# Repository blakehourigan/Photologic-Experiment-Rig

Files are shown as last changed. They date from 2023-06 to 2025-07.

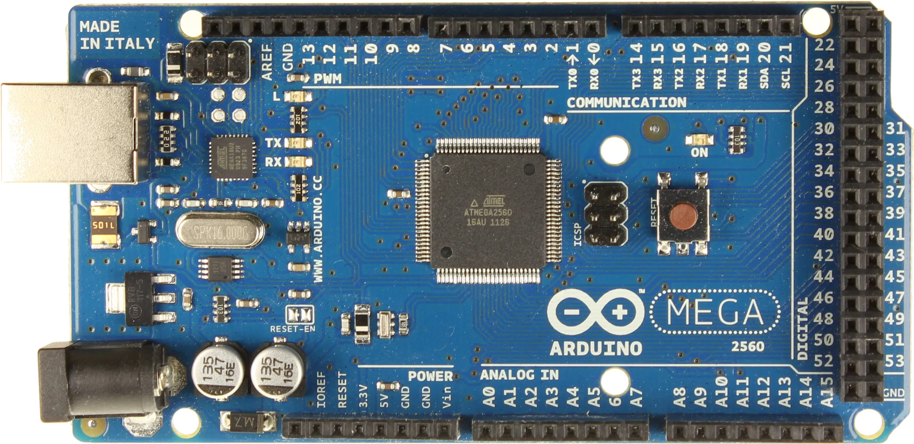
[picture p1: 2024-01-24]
Circuitry/Arduino-Mega-2560-Pinout.jpg

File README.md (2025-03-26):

# Samuelsen Lab Photologic-Experiment-Rig

## Overview
This project was created to enable novel experiments regarding smell and taste in Dr. Chad Samuelsen's research laboratory. The primary improvements that this rig provide include a photologic lick detection mechanism, and a simplified, non-motorized approach to stimulus delivery providing a more reliable experience during experimentation. 

This repository contains all files needed to reproduce a experimental rig of this type, including all 3d models, CNC machining files, code, and circuit design. 

## Features
-  **Data Accuracy** - Important event timing data such as onset, end, duration, onset relative to program start, and onset relative to trial start is measured **on Arduino Mega 2560 device** as these events occur. This ensured event timing results are accurate as viewed in the controller program.
-  **Data Representation** - Licks can be analyzed via a built in lick rasterization plot. This allows for simple visual verification of lick times relative to one another. One can ensure that licks are not occuring too close or too far apart in time. 
-  **Individual Valve / Motor Control** - Users can control each connected valve, opening or closing valves for arbitrary amounts of time. Users can also command the door motor to move up or down at any time. 
-  **Lick/Valve Prohibition** - Lick detection and valve actuation are decoupled events. A lick initiates a valve actuation, however, another lick CANNOT be detected until BOTH the valve has been closed from previous actuation AND tongue has cleared the beam (beam has restored a connection). This helps to avoid licks from occuring too close in succession. Furthermore, a continued beam break does not result in a continuous stream from a valve. A lick initiation will result in a valve opening of the determined length. This will not happen again until beam is restored and broken again. 
-  **Phantom Lick Removal** - Licks that complete in less than 10ms are disregarded and not sent to the controller (PC). This helps avoid invalid licks (due to equipment quirks) being recorded.  
-  **Simplicity** - Significant effort has been expended to ensure that software is easy to install and use. The previous model of using two Arduino boards to control the rig was found to be unnecessary. It was found to be far more effiecient to move to a one Arduino model, simplifying physical setup and communication protocols. 
-  **Speed** - Multiple threads (many cpu workers) are utilized so that GUI is always responsive regardless of logic operations underway at a given moment, without affecting the efficiency of those logic operations. 

### Required Physical Materials

- 1 Arduino Mega 2560
- 1 PC Controller Computer
- 1 Motor Logic Circuit Board
- 1 Experiment Box (3D CAD and CNC files included in this repository)
- 2 - 16 Valves and Cylinders 
 
### Assembly Instructions / Requirements for a Functioning Rig
1. **Rig Controller Code**

   **Documentation for the Rig Controller Code can be found [at this link.](https://blakehourigan.github.io/Photologic-Experiment-Rig/)**
    #### Prerequisites / Dependencies
    To use this program with the Arduino board controlling the rig peripherals (motors, optical sensors, etc) on a Windows machine, you **must** have the Arduino IDE installed. Failing to meet this dependency will result in the Arduino boards failure to connect to the controlling computer. 
    
    #### Windows Installation 
    To install the program on windows, there are two options. 
    
    1. **Exe Installer File** - To simplify this portion of the rig assembly / installation, a simple .exe installer has been provided. It can be found [here](https://github.com/blakehourigan/Photologic-Experiment-Rig/releases/tag/v1.0).
    
    2. **Running the Source Code** - For those that would rather run the program via source code, the process for getting the source code up and running can be found below.
        1. **Install Python 3.12** - This program was developed with Python version 3.12. This program is NOT guaranteed to work with any versions other than Python3.12. It can be installed [here](https://www.python.org/downloads/release/python-3120/).
        2. **Clone this repository locally on your computer** - Either by using git clone on your machine, or by clicking the 'code' dropdown on the homepage of this Github repo and downloading the .zip file, download this repository onto your machine.
        3. **Setup the Virtual Environment** - Once you have the repo locally on your machine, navigate to the controller code directory at `Photologic-Experiment-Rig\Code\Photologic Rig Main Application Code`. Once here, you can setup a virtual environment that will contain all depencies for the program by running the following command in a terminal window at this directory: `python -m venv venv'. This may take a few moments.
        4. **Activate the Environment** - Once the virtual environment is setup, you can activate it by running the following command.
            - **Windows** -> `venv\Scripts\Activate`
            - **Linux** -> `source venv/bin/activate `
        6. **Install the Dependencies** - This program is dependent on many external libraries to function properly. Under the 'Photologic Rig Main Application Code' directory, you will also find a file called requirements.txt. It contains all depencencies and their versions in a simple text file. You can install all of these dependencies at once by running the command `pip install -r requirements.txt`.
        7. **Run the Program** - You are now ready to run the controller program. Locate the file 'main.py' under the /src directory and run it by running the command `python main.py`, the program should now startup.

    #### Running the Program on Linux-based Systems
    There is no installation file for linux-based systems. Follow the 'Running the Source Code' steps described above.

    #### Building an Executable for a New Version of the Program
    For those that create new versions of the program to better suit their needs or to fix bugs that will undoubdedly arise through the usage of this program, a [Github Gist](https://gist.github.com/blakehourigan/5e176f2600446a793547babff372299c) has been put together detailing the steps you can take to create a new executable file and installer that will make installation/distribution of the program much simpler. 
    
3. **Arduino Code**
    #### Prerequisites / Dependencies
    To upload this code, you will need either the arduino-cli or the Arduino IDE. The Arduino IDE will be easiest to work with and can be found [here](https://www.arduino.cc/en/software).

    On Windows machines, the Arduino IDE is an optional package in the control software Exe installer discussed above.

    If you choose to use the Arduino IDE, you must follow these steps to ensure smooth upload of this code to the Arduino, and proper communication between the Arduino and the control software.
    #### IDE Configuration and Code Upload
    1. Once the Arduino IDE is installed, open the IDE with the Arduino Mega 2560 board connected to your PC. Your PC will recognize the board and the packages that it needs to install to communicate with it. There will be multiple pop-up windows asking if you would like to install drivers for this board. You **must** click install on all of these pop-ups. If you do not see these pop-ups and have used your Arduino board previously, you may have these packages already installed, try moving to the next step. 
    2. The code used for the Arduino in this project has one external dependency that must be fulfilled. This external dependency is the **AccelStepper** library by Mike McCauley. The version in use at the time of writing is version 1.64. You will need to install this version in the IDE. To do this, look for the library icon on the left hand side of the Arduino IDE window. It is the third button down. Once clicked, a slide-out window with the heading 'library manager' will open with a search box at the top. Click inside of the search bar and enter 'AccelStepper'. The first result should be the one you are looking for. Click the box filled with the version number (something like 1.64), and look for version 1.64. Click on this version, then click install, it should install rather quickly. Now you can now exit the library manager.
    3. Now, the Arduino code may be uploaded to the board. In the top left hand corner, click 'File', then 'Open', and search for the ArduinoCode directory in the Photologic-Experiment-Rig structure. The file you are looking for will be found at `Photologic-Experiment-Rig/Code/ArduinoCode/ArduinoCode.ino`. Locate this .ino file and double click on it to select it.
    4. Once this file is open in the IDE, ensure that your board is recognized and selected in the IDE by clicking the dropdown menu just below the 'help' section of the top bar. Here you will see any Arduino boards recognized by the PC. Select your Arduino Mega 2560 board.
    5. With the file open and your board selected, press the green upload button. It is the arrow that looks like this: '-->', the second button of three in the top left hand side of your screen. This will just take a moment, and you will see a 'Done Uploading' message in the bottom right of your screen if it completes successfully.

       **NOTE** - If you see lots of red messages and this code does not upload successfully, please make absolutely sure you installed the 'ArduinoStepper' library and that the board is connected **and** selected. You might try the board selection dropdown again to make sure of this. If this does not work, try disconnecting and reconnecting the board, and restarting your PC. 
    7. At this point your Arduino board and your PC are ready to communicate with each other for your experiments. 
 
4. **3D Printing:**

   Under contruction

5. **Machining:**   

   Under Contruction 

6. **Assembly:** 

   Under contruction

7. **Optical Fiber Setup:**   

   Under contruction

8. **Circuitry:** 

   Under contruction 

### Configuration

how to configure the system once assembled.

## Usage
A **SOP** (Standard Operating Procedure) for using this rig in an experiment can be found [here]().

## Navigating the Directory Structure
Each subdirectory in this project contains a README that explains the structure of the files contained within.

## License

This project is licensed under the MIT License - see LICENSE.txt for details.

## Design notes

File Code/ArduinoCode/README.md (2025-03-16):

# Arduino Source Code Directory

## Overview

This directory contains the code designed for the Arduino board that runs the motorized components of the 
photologic experiment rig. All licks, valve actuations, and door motor movements are orchestrated here.

## Directory Structure

An attempt was made to organize this structure such that each major component of the program is easy to find. 

### Project Root 

The project root contains the primary Arduino .ino file (comperable to main.py). This is the entry file of the program,
and can be thought of as the primary 'controller' for the Arduino code. It contains the standard 'setup' and 'loop' code 
included with most Arduino programs. 

The setup method defines input and output pins used throughout the program, while loop is the mainloop that runs continuously 
to listen for commands from the python controller program.

### Src Directory 

This directory contains headers and implementations for all primary aspects of the program. While the root file simply calls
logical functions, these directories and files provide the implementation for all this logic. 

**exp_init** - Contains logic regarding program initialization including receiving important program variables such as 
the valve schedules and opening durations for each side, as well and number of valves in use and number of trials.

**optical_detection** - This directory contains functions that detect breaks and reconnections in the optical beam, as well 
as updating the state of the lick indicator leds.

**reporting** - Here you'll find files that define the structure of the data reporting of the Arduino. It calculates event 
timing and sends it back to the controller program.

**valve_control** - Contains methods for interacting with valves. Includes methods for opening /closing single vs many valves.

**valve_testing** - Contains the logic for valve testing procedure as well as valve priming functionality.

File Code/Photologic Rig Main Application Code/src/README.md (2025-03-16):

# Source Code Directory Structure

This directory contains all source code for the program, as well as all configuration dependencies that are needed to run the program. These configuration files, along with other program 'assets' such as the program rat icon are located here. 

## MVC Architechture
An attempt was made to follow the Model-View-Controller architechture as closely as possible. In this model, 
the controller files manage interation between different components of the program. For example, models (data) 
should not interact directly with any view (GUI windows). These interations are instead managed through controller 
files. Somewhat confusingly then, the main 'controller' in this program is not in the controller directory but is 
instead called 'app_logic' and resides in the root of the /src directory. I felt this made the most sense as 
it is the source or the root of all other actions and files. As such it is placed at the root.

## Models
The models are the first classes instantiated when the program starts because all other classes require some access 
to the data that is held here. Global program variables that are passed around to various classes during 
program and experiment execution are stored here. Here you'll find data specific to different parts of the program, 
including 'experiment_process_data.py' where data regarding experiment specific data such as schedule generation, 
maximum runtime calculations, program schedule dataframe data (trial, licks per port, stimuli on a given trial, etc),
etc.

Continuing along these lines you'll find data specific to the arduino, detailed data on program events (door movements, lick times), and stimuli specific data in their respective directories.

## Views 
Finally, you'll find the views directory. As you might imagine, this directory contains all code involving the 
interactive Graphical User Interface (GUI). Every peice of code that defines something that a user interacts with 
or looks at is defined here. As before, the files have descriptive names that reveal which task they perform. 

## Controllers
This directory contains controllers other than the primary controller. Which at the time of writing contains only
the Arduino controller files. This handles interactions between Aduino specific data (models/arduino_data.py) and
Arduino specific actions. The primary action handled here is communication between the Arduino board and this 
program.

I hope that this structure proves easy to understand and navigate. I thought a lot about, and worked hard to ensure
that this would be the case.

-BH

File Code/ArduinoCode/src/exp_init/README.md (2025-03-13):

# Experiment Initialization Code

## The code in this directory is related to variables and functions that prepare the arduino for a new experiment.

### Primary functions include:

- Recieve experiment variables such as number of experiment trials and number of experiment stimuli. 
- Experiment variables allow the Arduino to safely receive the experiment valve schedule so that the required valves actuate during their assigned trial(s).
- Experiment variables also allow for safe receiving of valve opening time durations so that the Arduino knows how long to leave a valve open to get a desired 
amount of stimulant (generally 5 microliters).

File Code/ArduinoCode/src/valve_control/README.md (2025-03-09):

## VALVE CONTROL Motor Arduino Code 
This dir contains code that is designed to actuate the experiment stimuli valves. The lick_handler method is called from MotorArduinoCode.ino
and is passes a valve number (0-7), a PORT, and a duration. The code then decides which valve to actuate given valve_num, num_stimuli, and PORT.

The code will delay here for the duration passed in to the file, then will untoggle all valves and return control to MotorArduinoCode.ino.

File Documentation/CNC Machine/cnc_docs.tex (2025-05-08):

\documentclass{article}

\usepackage{hyperref}
\usepackage{listings}
\usepackage{xcolor}
\usepackage{graphicx}
\usepackage{subcaption}
\usepackage{placeins}
\usepackage{pdfpages}

\graphicspath{{"/home/blake/Pictures/arduino migration guide"}}

\setlength{\parskip}{1em}

\title{Samuelsen Lab \\ CNC Machine Operation}
\author{Blake Hourigan}
\date{April 28, 2025}

\lstset{
    basicstyle=\ttfamily\small,
    breaklines=true,
    numbers=left,
    numberstyle=\tiny,
    frame=single,
    keywordstyle=\color{blue},
    commentstyle=\color{gray},
    stringstyle=\color{orange},
}
\lstdefinelanguage{yaml}{
    morekeywords={true,false,null,y,n},      % Add keywords here
    sensitive=false,                        % Case insensitive
    morecomment=[l]{\#},                    % Line comments start with #
    morestring=[b]",                        % Double-quoted strings
    morestring=[b]',                        % Single-quoted strings
}

\begin{document}
\maketitle
\clearpage
\tableofcontents
\clearpage

\section{Obtain a Model to Machine}
Before telling the machine what path to take and what setting to use to cut out a certain part, the user must decide which part to cut, find the Solidworks part file or Fusion360 `step' file, 
generate a `drawing' (dxf) file and then layout this drawing file in the 'Carbide Create' application so that machine understands what part is being cut out, how large the stock piece is, 
and where to cut into this stock piece. 

An exception to this general rule is the case where a `C2D' toolhead path file has already been generated for a given part. If this is the case for your part, skip to Section... REFERENCE 
THE SECTION FOR CHECKING AND RUNNING AN OPERATION HERE!!!!!!!!!!!!!!!!!!!!! An example of when this will be the case includes the CNC files for all models created for the `Photologic 
Experiment Rig' and can be found in the `Rig Assembly Files' directory of the Rig's GitHub repo found \href{https://github.com/blakehourigan/Photologic-Experiment-Rig}{here}.

\section{Obtain a Drawing File for this Model}

\section{Toolhead Settings for Given Materials}

\section{Fixing the Materials to the Machine}
\section{Running a .C2D File on the CNC Machine}

\end{document}

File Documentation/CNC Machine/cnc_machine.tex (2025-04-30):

\documentclass{article}

\usepackage{hyperref}
\usepackage{listings}
\usepackage{xcolor}
\usepackage{graphicx}
\usepackage{subcaption}
\usepackage{placeins}
\usepackage{pdfpages}

\graphicspath{{"/home/blake/Pictures/arduino migration guide"}}

\setlength{\parskip}{1em}

\title{Samuelsen Lab\\CNC Machine User Guide}
\author{Blake Hourigan}
\date{April 30, 2025}

\lstset{
    basicstyle=\ttfamily\small,
    breaklines=true,
    numbers=left,
    numberstyle=\tiny,
    frame=single,
    keywordstyle=\color{blue},
    commentstyle=\color{gray},
    stringstyle=\color{orange},
}
\lstdefinelanguage{yaml}{
    morekeywords={true,false,null,y,n},      % Add keywords here
    sensitive=false,                        % Case insensitive
    morecomment=[l]{\#},                    % Line comments start with #
    morestring=[b]",                        % Double-quoted strings
    morestring=[b]',                        % Single-quoted strings
}

\begin{document}
\maketitle
\clearpage
\tableofcontents
\clearpage

\section{Sourcing a Part File (Finding the File to Cut a Shape)}
\subsection{The End Goal}
What you will eventually need to obtain to run a cutting operation on the Shapeoko Pro CNC machine is a \textit{C2D} file. You can identify these files
by their file \textit{extension}. What this means is that CNC machine files will look something like \textit{`part\_name\_here.c2d'}.

Some parts, especially those which have already been cut out before using the Shapeoko Pro CNC machine will already have a c2d file (also referred to 
in this document as a \textit{toolpath} file). If this is the case and you have located the C2D file for your part you can move on to Section 
\ref{sec:verifying-toolpath}, where the process of verifying and modifying existing toolpaths is detailed.

For newly created parts, a C2D file will not exist. You will need to obtain or create a \textit{part file} containting the dimensions of the part 
that you would like to cut out. Then, from this part file, you will need to generate a \textit{`dxf'} file. This `dxf' file will contain the 
two-dimensional representation of some `face' of a part, which will allow you to create a `toolpath' that will cut this `face' out from your stock. 

So, to briefly summarize, to cut a part out from a piece of stock on the Shapeoko Pro CNC Machine, you need a C2D file. This file may or may not already
exist. If it does exist and you have located the file, you can modify this for your particular piece of stock and cut it out. If it does not exist you
will need to create it. To create a C2D you need:
\begin{itemize}
    \item A part file (Solidworks SLDPRT or Fusion360 STEP). This can be created by you or sourced from online. But you need to be reasonable about 
        what you can cut out on our machine. The simpler the better.
    \item A \textit{dxf} file. This is a 2d representation of some side or `face' of the part that can be cut out by the CNC. 
\end{itemize}

Once you have obtained the dxf file, you can place it in a tool called \textit{Carbide Create} to define the toolpath. This is discussed further 
in Section \ref{sec:create-toolpath}.

\subsection{What is a Part File?}
A part file is a file used for 3d modelling purposes. There are many types of files such as \textit{SLDPRT} files, \textit{STEP} files, \textit{STL} files
and more. These are all similar in that they represent a 3d object in digital form. Most importantly for our use case, they contain information about 
objects including the \textit{dimensions} of the part we would like to cut out in the real world. 

\subsection{Where do Part Files Come From?}
The type of file that interests us for the purposes of creating a C2D file are SLDPRT files, which are files created for parts inside of the 
Solidworks 3d modelling program, OR STEP files, which can be used in Solidworks or Autodesk Fusion360. These parts can be created by you or someone 
else in the lab, or can be downloaded from the internet. The important part is that the file is a SLDPRT or STEP file.

\subsection{Obtaining the DXF File}
Both Solidworks and Fusion360 have... 

\subsubsection{Obtaining the DXF File from Solidworks}

\subsubsection{Obtaining the DXF File from Fusion360}

\section{Creating a Toolpath (Making a C2D File)}
\label{sec:create-toolpath}

\subsection{What is a Toolpath?}
A toolpath, as has been referred to many times in this guide, is the path the toolhead/router/machine bit will take to cut out your part. This file 
contains not only the path however, but also the \textit{feed rate}, which is the rate at which router will move around the material, 
\textit{plunge rate}, which is the rate at which the tool will move vertically into the material, 
\textit{RPM of the spindle} which is the rate at which the spindle will rotate during certain portions of the operation, etc. 

All of these attributes are important to get right to get a good finish from your operation. They also change depending on what \textit{material} you 
are cutting. Settings that have been found to work well with the two primary materials that are cut in the lab are discussed in detail in 
Secition \ref{sec:modifying-toolpath-attr}.

\subsection{What Tools will I Use?}

\subsection{Verifying Toolpaths}
\label{sec:verifying-toolpath}

\subsection{Modifying Aluminum Toolpath Attributes}
\label{sec:modifying-toolpath-attr}

As mentioned previously, it is important to get the \textit{attributes} of the toolpath such as selected tool, Spindle RPM, feed rate, etc in the 
proper ranges for your material to ensure a sucessful cut and a clean finish around cutting edges. 

Here, we will discuss the proper settings for operations involving \textit{Aluminum}.

\subsubsection{Selecting a Tool}
In this section we discuss which tool/bit/mill to use for an operation. This is a rather simple choice compared to the other attributes, and comes down
to the size of cuts you are making with your part. Generally, a .25" end mill/bit works perfectly well for machining operations. However, scenarios 
often arise where this mill will not produce successful cuts, such as when a user wants to cut a hole less than .25" in diameter. A .25" end mill simple 
will not physically fit into this hole and therefore will not work.

In other words, the .25" end mill is useful for all cuts where it physically fits in your cutting path. If this is not the case, another end mill would 
be of use. At the time of writing this guide in April of 2025, the end mill often used as a substitute is the 1/8" end mill. 

\subsubsection{Feed Rate}

\subsubsection{Plunge Rate}

\subsubsection{Spindle RPM}

\subsection{Modifying Acryllic Toolpath Attributes}

\subsubsection{Selecting a Tool}

\subsubsection{Feed Rate}

\subsubsection{Plunge Rate}

\subsubsection{Spindle RPM}

\section{Securing the Part to the Cutting Board}
This part of the process is mostly independent of the material that you will be cutting, but one must be mindful of the material througout the 
process. This will be discussed in more detail when relevent below.

\section{Securing the Part Using Tape}

\section{Securing the Part Using Glue}
This method is generally most useful when cutting aluminum, but can be very useful with acryllic as well. When possible, it is more efficient to avoid 
using the glue method because one must clean the cutting board thoroughly each time a new stock piece (piece of material that you cut a part out of) is 
placed on the cutting board. Furthermore, one must glue the piece to the cutting board and wait for the glue to \textit{cure} which takes about 30
minutes until the part is secure enough to stay put through an entire tool path cycle.

For most acryllic tool paths, the tape method described previously works fantastically well and can be much quicker and more efficient than using the 
glue method with all its overhead. If a tool path is very complex, using much or most of the area of the stock piece, it may be useful to use the glue
method. When using aluminum, the glue method can be incredibly useful to keep the entire sheet as level as possible, which is important to achieve 
clean cuts on all cut edges.

\end{document}

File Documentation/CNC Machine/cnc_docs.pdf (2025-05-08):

# Samuelsen Lab CNC Machine Operation

Blake Hourigan

April 28, 2025

1

## Contents

1 Obtain a Model to Machine | 3
2 Obtain a Drawing File for this Model | 3
3 Toolhead Settings for Given Materials | 3
4 Fixing the Materials to the Machine | 3
5 Running a .C2D File on the CNC Machine | 3

2

## 1 Obtain a Model to Machine

Before telling the machine what path to take and what setting to use to cut out a certain part, the user must decide which part to cut, find the Solidworks part file or Fusion360 ‘step’ file, generate a ‘drawing’ (dxf) file and then layout this drawing file in the ’Carbide Create’ application so that machine understands what part is being cut out, how large the stock piece is, and where to cut into this stock piece.

An exception to this general rule is the case where a ‘C2D’ toolhead path file has already been generated for a given part. If this is the case for your part, skip to Section... REFERENCE THE SECTION FOR CHECKING AND RUNNING AN OPERATION HERE!!!!!!!!!!!!!!!!!!!!! An example of when this will be the case includes the CNC files for all models created for the ‘Photologic Experiment Rig’ and can be found in the ‘Rig Assembly Files’ of the Rig’s GitHub repo found here. (https://github.com/blakehourigan/Photologic-Experiment-Rig)

## 2 Obtain a Drawing File for this Model

## 3 Toolhead Settings for Given Materials

## 4 Fixing the Materials to the Machine

## 5 Running a .C2D File on the CNC Machine

3

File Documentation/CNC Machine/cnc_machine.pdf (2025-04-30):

# Samuelsen Lab CNC Machine User Guide

Blake Hourigan

April 30, 2025

1

## Contents

1 Sourcing a Part File (Finding the File to Cut a Shape) | 4
2 Creating a Toolpath (Making a C2D File) | 5
3 Securing the Part to the Cutting Board | 6

2

4 Securing the Part Using Tape | 7
5 Securing the Part Using Glue | 7

3

## 1 Sourcing a Part File (Finding the File to Cut a Shape)

### 1.1 The End Goal

What you will eventually need to obtain to run a cutting operation on the Shapeoko Pro CNC machine is a C2D file. You can identify these files by their file extension. What this means is that CNC machine files will look something like ‘part name here.c2d’.

Some parts, especially those which have already been cut out before using the Shapeoko Pro CNC machine will already have a c2d file (also referred to in this document as a toolpath file). If this is the case and you have located the C2D file for your part you can move on to Section 2.3, where the process of verifying and modifying existing toolpaths is detailed.

For newly created parts, a C2D file will not exist. You will need to obtain or create a part file containting the dimensions of the part that you would like to cut out. Then, from this part file, you will need to generate a ‘dxf ’ file. This ‘dxf’ file will contain the two-dimensional representation of some ‘face’ of a part, which will allow you to create a ‘toolpath’ that will cut this ‘face’ out from your stock.

So, to briefly summarize, to cut a part out from a piece of stock on the Shapeoko Pro CNC Machine, you need a C2D file. This file may or may not already exist. If it does exist and you have located the file, you can modify this for your particular piece of stock and cut it out. If it does not exist you will need to create it. To create a C2D you need:

- A part file (Solidworks SLDPRT or Fusion360 STEP). This can be created by you or sourced from online. But you need to be reasonable about what you can cut out on our machine. The simpler the better.
- A dxf file. This is a 2d representation of some side or ‘face’ of the part that can be cut out by the CNC.

Once you have obtained the dxf file, you can place it in a tool called Carbide Create to define the toolpath. This is discussed further in Section 2.

### 1.2 What is a Part File?

A part file is a file used for 3d modelling purposes. There are many types of files such as SLDPRT files, STEP files, STL files and more. These are all similar in

4

that they represent a 3d object in digital form. Most importantly for our use case, they contain information about objects including the dimensions of the part we would like to cut out in the real world.

### 1.3 Where do Part Files Come From?

The type of file that interests us for the purposes of creating a C2D file are SLDPRT files, which are files created for parts inside of the Solidworks 3d modelling program, OR STEP files, which can be used in Solidworks or Autodesk Fusion360. These parts can be created by you or someone else in the lab, or can be downloaded from the internet. The important part is that the file is a SLDPRT or STEP file.

### 1.4 Obtaining the DXF File

Both Solidworks and Fusion360 have...

### 1.4.1 Obtaining the DXF File from Solidworks

### 1.4.2 Obtaining the DXF File from Fusion360

## 2 Creating a Toolpath (Making a C2D File)

### 2.1 What is a Toolpath?

A toolpath, as has been referred to many times in this guide, is the path the toolhead/router/machine bit will take to cut out your part. This file contains not only the path however, but also the feed rate, which is the rate at which router will move around the material, plunge rate, which is the rate at which the tool will move vertically into the material, RPM of the spindle which is the rate at which the spindle will rotate during certain portions of the operation, etc.

All of these attributes are important to get right to get a good finish from your operation. They also change depending on what material you are cutting. Settings that have been found to work well with the two primary materials that are cut in the lab are discussed in detail in Secition 2.4.

5

### 2.2 What Tools will I Use?

### 2.3 Verifying Toolpaths

### 2.4 Modifying Aluminum Toolpath Attributes

As mentioned previously, it is important to get the attributes of the toolpath such as selected tool, Spindle RPM, feed rate, etc in the proper ranges for your material to ensure a sucessful cut and a clean finish around cutting edges.

Here, we will discuss the proper settings for operations involving Aluminum.

### 2.4.1 Selecting a Tool

### 2.4.2 Feed Rate

### 2.4.3 Plunge Rate

### 2.4.4 Spindle RPM

### 2.5 Modifying Acryllic Toolpath Attributes

### 2.5.1 Selecting a Tool

### 2.5.2 Feed Rate

### 2.5.3 Plunge Rate

### 2.5.4 Spindle RPM

## 3 Securing the Part to the Cutting Board

This part of the process is mostly independent of the material that you will be cutting, but one must be mindful of the material througout the process. This will be discussed in more detail when relevent below.

6

## 4 Securing the Part Using Tape

## 5 Securing the Part Using Glue

This method is generally most useful when cutting aluminum, but can be very useful with acryllic as well. When possible, it is more efficient to avoid using the glue method because one must clean the cutting board thoroughly each time a new stock piece (piece of material that you cut a part out of) is placed on the cutting board. Furthermore, one must glue the piece to the cutting board and wait for the glue to cure which takes about 30 minutes until the part is secure enough to stay put through an entire tool path cycle.

For most acryllic tool paths, the tape method described previously works fantastically well and can be much quicker and more efficient than using the glue method with all its overhead. If a tool path is very complex, using much or most of the area of the stock piece, it may be useful to use the glue method. When using aluminum, the glue method can be incredibly useful to keep the entire sheet as level as possible, which is important to achieve clean cuts on all cut edges.

7

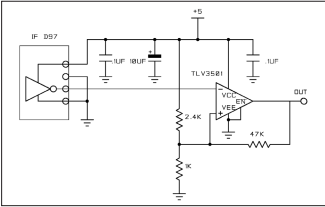
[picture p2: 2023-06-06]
Circuitry/Lick Detection Circuitry.png

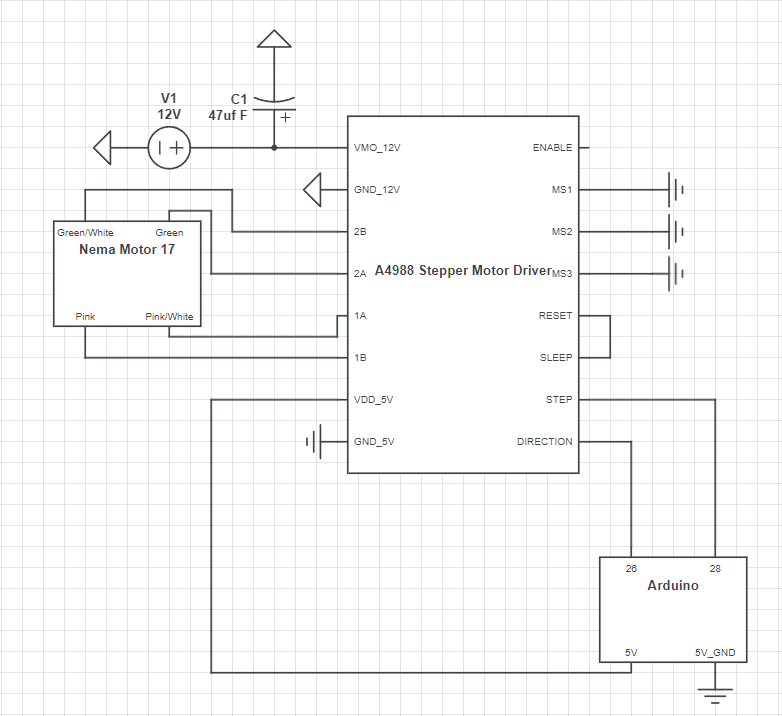
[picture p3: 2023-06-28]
Circuitry/Motor_circuit.png

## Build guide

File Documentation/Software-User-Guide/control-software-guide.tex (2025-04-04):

\documentclass{article}

\usepackage{hyperref}
\usepackage{listings}
\usepackage{xcolor}
\usepackage{graphicx}
\usepackage{subcaption}
\usepackage{placeins}
\usepackage{pdfpages}
\usepackage{xcolor}    % Required for specifying colors
\usepackage{textcomp}  % Recommended for proper straight quotes, etc.
\usepackage[T1]{fontenc}

% --- Define colors for syntax highlighting ---
\definecolor{codegreen}{rgb}{0,0.6,0}
\definecolor{codegray}{rgb}{0.5,0.5,0.5}
\definecolor{codepurple}{rgb}{0.58,0,0.82}
\definecolor{backcolour}{rgb}{0.95,0.95,0.92} % A light background color

% --- Define a custom listings style for Python ---
\lstdefinestyle{mystyle}{
    backgroundcolor=\color{backcolour},
    commentstyle=\color{codegreen},
    keywordstyle=\color{magenta},
    numberstyle=\tiny\color{codegray},
    stringstyle=\color{codepurple},
    basicstyle=\ttfamily\footnotesize, % Use typewriter font, slightly smaller
    breakatwhitespace=false,
    breaklines=true,                 % Automatically break long lines
    captionpos=b,                    % Caption position: bottom
    keepspaces=true,                 % Keep spaces, important for indentation
    numbers=left,                    % Line numbers on the left
    numbersep=5pt,                   % Distance of numbers from code
    showspaces=false,                % Don't show spaces as special characters
    showstringspaces=false,          % Don't show spaces in strings differently
    showtabs=false,                  % Don't show tabs as special characters
    tabsize=4,                       % Set tab width (Python standard is 4)
    language=Python,                 % Set the language
    morekeywords={self, dict, int},  % Add specific keywords if needed
    frame=single,                    % Add a frame around the code
    rulecolor=\color{black},         % Color of the frame
    upquote=true                     % Ensure straight quotes are used correctly
}
\graphicspath{{"/home/blake/Pictures/software-user-guide"}}

\setlength{\parskip}{1em}

\title{\textbf{Photologic Experiment Rig}\\Control Software User Guide}
\author{Blake Hourigan}
\date{March 30, 2025}

\lstset{
    basicstyle=\ttfamily\small,
    breaklines=true,
    numbers=left,
    numberstyle=\tiny,
    frame=single,
    keywordstyle=\color{blue},
    commentstyle=\color{gray},
    stringstyle=\color{orange},
}
\lstdefinelanguage{yaml}{
    morekeywords={true,false,null,y,n},      % Add keywords here
    sensitive=false,                        % Case insensitive
    morecomment=[l]{\#},                    % Line comments start with #
    morestring=[b]",                        % Double-quoted strings
    morestring=[b]',                        % Single-quoted strings
}

\begin{document}
\maketitle
\clearpage
\tableofcontents
\clearpage

\section{Introduction}
This guide provides simple overviews of included features in the Photologic-Experiment-Rig control software. It also explains the specifics of these features and how to use 
them. Some features may not have robust explanations within the software as to what \textit{type/unit} of value goes in a text box, 
what a certain value displayed in a menu means, among other various confusions. 

This guide is intended to make up for areas of the program that may lack in clarity. Each primary user interface window has its own section here that you can jump
to using the table of contents. 

\section{Installing the Software}
\label{sec:installation}
An installation guide for all software required to get the rig up and running has been written in another article. For convenience this is provided in the pages that follow.
Because the guide included is a PDF in itself, the page numbers will appear out of order until the software guide is complete.
\includepdf[pages=10-16]{"/home/blake/Documents/Photologic-Experiment-Rig/Documentation/Arduino Migration Guide/arduino_migration_guide.pdf"} 
%\FloatBarrier

\section{The Main Control Window}
\label{sec:main-control}
The `Main Control Window' refers to the user interface window that appears first upon application startup. This window is the heart of the program and is where much of the 
required experiment configuration will take place. This window is shown below in Figure \ref{fig:main-screen}. 

This window can be broken down into 5 primary sub-sections, and as such, this section of the guide is broken down into sub-sections that reflect this layout. 

\begin{figure}[h!]
        \centering
        
        \caption{The `Main Control Window' is the root of all application logic and sub-windows. It allows for navigation to these sub-windows, 
        and allows users to configure and begin experiments.}
        \label{fig:main-screen}
\end{figure}
\FloatBarrier

\newpage
\subsection{Row 1 - Start and Reset}
Row 1 contains two of the most important buttons in the application interface. Start/Stop allows a user to command the program to begin or 
terminate an experiment depending on current state. Reset allows the user to clear \textbf{all existing experiment data} and ready the application 
for a new experiment run. 

\subsubsection{Start and Stop (an Experiment)}
\label{sec:start-exp}
The start button is important because it allows the user to begin or end an experiment. Before the user can begin an experiment, 
the experiment must be fully configured. This means that all of the following steps must be completed to continue: 
\begin{enumerate}
    \item Base state  interval times (ITI, TTC, Sample, etc.), random interval times (+/- ITI, +/- TTC, +/- Sample, etc.) 
        and other configuration variables (\# Trial Blocks, \# Stimuli) \textbf{must} be defined. Discussed in Section \ref{sec:basic-configuration}.
    \item All valves must be configured with corresponding stimulus names in the `Valve / Stimuli' window. Discussed in depth in Section 
        \ref{sec:valve-stim-window}.
    \item The program schedule must be generated. Discussed in depth in Section 
        \ref{sec:valve-stim-window}.
\end{enumerate}

Once all of these requirements have been fulfilled the user can begin an experiment run. If a step has been missed, or something has 
gone wrong, the user may see a warning message such as the one in Figure \ref{fig:no-schedule}. This indicates that the program stimuli schedule has not 
yet been generated, and that the user should re-visit the 'Valve / Stimuli' window (Section \ref{sec:valve-stim-window}) 
to attempt a proper schedule generation.

If a experiment run has been started, the `Start' button will be changed to a stop button as shown in Figure \ref{fig:stop-button}. 
Pressing this button will terminate the experiment early. This will begin the standard termination process. This includes:
\begin{itemize}
    \item Halting program execution. No further experiment operations will be taken. Door will not close, program state will be 
        switched to "IDLE".
    \item Terminating the connection to the Arudino board .
    \item Preparing all accumulated data to be saved. 
    \item The user will be prompted to optionally save this data via a pop-up window in a location of their chosing.
\end{itemize}

\begin{figure}[h!]
    \centering
    \begin{subfigure}[t]{.45\textwidth}
        \centering
        
        \caption{Without an Experiment Schedule, the program isn't sure what to do. You must generate a schedule following the steps above to run an experiment.}
        \label{fig:no-schedule}
    \end{subfigure}
    \hfill
    \begin{subfigure}[t]{.45\textwidth}
        \centering
        
        \caption{Start Button is Converted to Stop Button on Experiment Start.}
        \label{fig:stop-button}
    \end{subfigure}
    \caption{}
    \label{fig:pg_admin_figs}
\end{figure}
\FloatBarrier

\subsubsection{Reset (Preparing for a New Experiment)}
The other primary button in this row of the main window is the `Reset' button. This button is important because it is \textbf{required} after 
running an experiment that the user takes either of the two following actions:
\begin{enumerate}
    \item Presses the gray 'Reset' button in the main program window. 
    \item Use the familiar red Windows `X' in the corner of the main application window to close the application session and manually 
        restart by clicking the `Photologic-Experiment-Rig' control software icon on the desktop or in the taskbar. This is the icon 
        with a cartoon rat on it. 
\end{enumerate}

Both of these actions perform the same effective operation which is to clear the data from the previous experiment and get
the program ready for a new experiment. To reiterate, pressing `Reset' will \textbf{destroy all experiment data accumulated} if the user 
has not saved this data by pressing the `Save Data' button in the fifth row of the main experiment window since the last experiment was run.
This means the user should be \textbf{very careful} when pressing this button. 

It is for this reason that when a user presses the Reset button, a warning will be displayed as shown in Figure \ref{fig:reset-confirm}. If the user selects `Yes' in this 
popup window all data will be destroyed and all windows will be closed, then the main program window will re-open automatically, ready for a new experiment.
\newline
\newline
\textbf{NOTE:} This action cannot be performed unless an experiment is \textit{not currently running}. Otherwise, you must stop the current experiment and then reset the 
application.

\begin{figure}[h!]
        \centering
        
        \caption{User must Confirm a Reset Action before it will Execute to Prevent Accidental Loss of Data.}
        \label{fig:reset-confirm}
\end{figure}
\FloatBarrier

\newpage
\subsection{Row 2 - Program Timers}
The second row of the main program window features three timers that inform the user of the following pieces of information:
\begin{enumerate}
    \item \textbf{Time Elapsed}: How long the program has been running in total
    \item \textbf{State Time}: How long the program has been in the current state (ITI, TTC, DOOR OPEN, etc.).
    \item \textbf{Maximum Total Time}: Maximum amount of time the program can possibly run.
\end{enumerate}

These timers all begin at zero until the program schedule has been generated (discussed in Section \ref{sec:valve-stim-window}) and the user 
presses the `Start' button in the main experiment window. Once an experiment has begun, this row will be populated to reflect the real values 
that belong here as shown in Figure \ref{fig:timers}.

\begin{figure}[h!]
        \centering
        
        \caption{}
        \label{fig:timers}
\end{figure}
\FloatBarrier

\newpage
\subsubsection{Time Elapsed}
This timer is the primary timer for the currently running experiment. This timer shows the time elapsed since the moment the user pressed the start button. It follows a format
of `SS | MM:SS', where the `SS' before the format separator (`|') is the \textit{total seconds} elapsed since program start time. 

Because this is a bit unwieldy and perhaps unhelpful, the information following the separator `|' shows the same figure converted to minutes 
and seconds. This allows for an easier understanding at a glance of total experiment time elapsed.

\subsubsection{State Time}
The `State Time' timer keeps track not only of the amount of state time that has elapsed since the state began, but also the maximum time it could 
possible consume. The timer follows the format of `ELAPSED TIME / TOTAL AVAILABLE TIME'. 

The only time throughout an experiment when the `TOTAL TIME' figure \textit{may} not be met is during the `TTC' time. This time can be cut short if the rat chooses to engage
in the trial. Thus the state timer may end before reaching `TOTAL TIME'.

\subsubsection{Maximum Total Time}
The `Maximum Total Time' timer is included as a convenience function that gives the user a general idea of how long an experiment could possibly take. It is almost certain to 
be inaccurate and \textit{over-estimate} the amount of time an experiment will take, because it calculates this value by \textit{summing all base interval values and random 
interval values together}. 

This means that the program assumes that all intervals --- including TTC intervals --- will use \textbf{all} of their allocated time. This is
very unlikely to be true, as the rat is likely to engage in at least \textit{some} trials. However, it still gives a general idea of the length of time an experiment 
may take.

\newpage
\subsection{Row 3 - Status Indicators}
Row 3 contains many different experiment \textit{status indicators} that inform the user of the current values of important trial variables. 
These include:

\begin{itemize}
    \item \textbf{Status (Program State)}: This indicator informs the user of the current program state ("IDLE", "ITI", "TTC", etc.)
    \item \textbf{Trials Completed (Current Trial/Total Trials)}: Displays the current trial and total trials for this experiment. Includes 
        a progress indicator to show experiment progress at a glance.
    \item \textbf{Side One: \{Stimulus\} |VS| Side Two: \{Stimulus\}}: Current Stimulus Delivery per Port (Side): Inform user which stimulus 
        is being delivered on each port (side) for the current trial. 
\end{itemize}

Examples of what these indicators look like during an experiment run are shown in Figure \ref{fig:status-indicators}. 

\begin{figure}[h!]
        \centering
        
        \caption{Status Indicators Aid the User by Informing them of the Current State of Experiment Variables.}
        \label{fig:status-indicators}
\end{figure}
\FloatBarrier

\newpage
\subsection{Row 4 - Configuring the Experiment}
\label{sec:basic-configuration}
Row 4 is one of the rows in the main window that the user will interact with the most. This row is where the user enters any desired configuration changes for an upcoming 
experiment. This row and the contained entry widgets are shown in Figure \ref{fig:entry-widgets}. 

The primary experiment variables that may change from experiment to 
experiment are the base state intervals (ITI, TTC, Sample), random state intervals (+/- ITI, +/-, TTC, etc), `\# Trial Blocks' 
(number of times each possible stimulus pairing should be delivered), and `\# Stimuli' (number of valves in use). 

\begin{figure}[h!]
        \centering
        
        \caption{The Entry Widgets in the Main Window Allow the User to Modify Default Experiment Variables.}
        \label{fig:entry-widgets}
\end{figure}
\FloatBarrier

These variables should be changed \textbf{before} the schedule is generated for the experiment. 
\newline
\newline
\textbf{NOTE}: All \textit{time-related values} (interval times) must be given in \textbf{milliseconds}. For example, 30 seconds should be 
entered in as 30000 milliseconds. 
\newline
\newline
Ensure that no entry boxes are left \textit{empty} before generating the schedule. Each box needs to 
contain some \textit{positive integer} to correctly generate the experiment schedule.

\newpage
\subsubsection{Changing Default Values}
If the default values need to be modified, this requires a change in the Python codebase. This is an involved process 
because \href{https://gist.github.com/blakehourigan/5e176f2600446a793547babff372299c}{new versions of the program need to be compiled and 
built into a new installer.}

Default values are defined in the GitHub repository directory in the file found at subdirectory
`/Code/Photologic Rig Main Application Code/src/models/experiment\_process\_data.py'
under variables named self.interval\_vars, and self.exp\_var\_entries. 

This code is shown in Listing \ref{lst:python_dicts}. Defaults can be changed here, but again a new program build and installer must be created and 
installed onto the user's machine. Users may need to ask the lab tech for assistance in this process.

\begin{lstlisting}[style=mystyle, caption={Default values can be seen Above. Time-Related Interval Values are Separated from Other Values like Number of Trials.}, label={lst:python_dicts}]
self.interval_vars: dict[str, int] = {
    "ITI_var": 30000,
    "TTC_var": 20000,
    "sample_var": 15000,
    "ITI_random_entry": 0,
    "TTC_random_entry": 5000,
    "sample_random_entry": 5000,
}
self.exp_var_entries: dict[str, int] = {
    "Num Trial Blocks": 10,
    "Num Stimuli": 4,
    "Num Trials": 0,
}
\end{lstlisting}

\newpage
\subsection{Row 5 - Accessing Other Control Windows}
Row 5 of the main program window contains 7 gray buttons that allow for navigation to other important experiment control windows. 
(Figure \ref{fig:window-buttons})

\begin{figure}[h!]
        \centering
        
        \caption{The Buttons in Row 5 Allow for Navigation to Other Experiment Windows.}
        \label{fig:window-buttons}
\end{figure}
\FloatBarrier

Descriptions of buttons and their functions will begin on the first row and column of this section. Each button in a row will be described, then the next
row will be described.

\begin{enumerate}
    \item \textbf{Valve Testing / Prime Valves}: This button allows for navigation to the `Valve Testing / Prime Valves' window. A user would
        navigate here if they desired calibrating valve opening durations via the automatic testing procedure or if they desired to 
        `Prime' the valves prior to an experimnet run. This window is discussed in depth in Section \ref{sec:valve-testing-window}.
    \item \textbf{Valve Control}: This button allows for navigation to the `Valve Control' window. A user would navigate here if they 
        desired opening or closing valves for arbitrary lengths of time. This window also allows for the manual toggling of the rig's 
        door motor to the up or down position for arbitrary lengths of time. This window is discussed in depth in 
        Section \ref{sec:valve-control}.
    \item \textbf{Program Schedule}: This button allows for navigation to the `Program Schedule' window. This is where the user would find 
        most experiment data including:
        \begin{itemize}
            \item Trial block numbers.
            \item Trial numbers.
            \item Licks-per-port for a trial.
            \item Stimulus delivered on each side for a trial.
            \item ITI, TTC, Sample times for a trial.
        \end{itemize}
            This window is discussed in depth in Section \ref{sec:program-schedule}.
    % begin row 2 
    \item \textbf{Valve / Stimuli}: This button allows for navigation to the `Valve / Stimuli' window. This is where the user navigates to 
        assign stimuli names to specific valves for the experiment. This is required to generate the experiment schedule. This window 
        and associated functions are discussed in depth in Section \ref{sec:valve-stim-window}.
    \item \textbf{Event Data}: This button allows for navigation to the `Event Data' window. This is where all data not included in the 
        `Program Schedule' window is found. A user might navigate here to view detailed data about specific events that take place during the 
        program like licks or door motor movements. This window is discussed in depth in Section \ref{sec:event-data-window}.
    \item \textbf{Rasterized Data}: This button allows for navigation to the `Rasterized Data' window. A user might navigate here to view 
        lick data per trial in a raster plot. This window is discussed in depth in Section \ref{sec:rasterized-data-window}.
    \item \textbf{Save Data}: This button is used to save all currently held data into 2 separate excel spreadsheet files. Data in the program 
        is split into 2 primary `DataFrames'. These DataFrames include the `Program Schedule DataFrame' and the `Event Dataframe'. The data 
        stored in each frame is as described previously for each respective window corresponding to these DataFrames.
\end{enumerate}

\newpage
\section{`Valve Testing / Prime Valves' Window}
\label{sec:valve-testing-window}
This window is where the user would navigate for valve opening duration calibration or valve `priming' before a experiment run. The 
`Valve Testing / Prime Valves' window is shown below in Figure \ref{fig:test-prime}.

\begin{figure}[h!]
        \centering
        
        \caption{The `Valve Testing / Prime Valves' Window opens in Testing Mode upon First Button Press.}
        \label{fig:test-prime}
\end{figure}
\FloatBarrier

\newpage

\subsection{Valve Open Duration Calibration (Running a Valve Test)}
\label{sec:valve-profiles-how-to}
This window opens in `Testing' mode by default. A user can be sure that they are in test mode if the large orange `Switch to Priming Mode' 
button is in view at the top of the window. 

In this window a user will notice several interface components that are critical to a
successful valve calibration. Calibration is important to run often to ensure that each valve is delivering the proper amount of stimulus 
on each valve in use during an experiment. The process of running a valve test procedure is described below.

\begin{enumerate}
    \item \textbf{Enter Desired Amount of Stimulus Per Lick}: First, the user should enter how much liquid that is desired each time the valve 
        opens in the entry box just below the label `Desired Dispensed Volume in Microliters (ul)'. The default value for this entry is 5
        microliters.
    \item \textbf{Enter Number of Valve Actuations}: Then, enter the number of times a valve should open and close for each test in the entry 
        box just below the label `How Many Times Should the Valve Actuate?'. 

        The default value for this entry is 1000 and is a good starting 
        point for testing. This attribute of the procedure is \textit{variable} in the event that a user wants to change this value, and 
        new duration calculations will adjust to the value input in this field. However, higher numbers will yield more accuration calculations.
    \item \textbf{Select Valves to be Tested}: Next, the user should select the valves to be tested during this procedure. This is done by 
        selecting valves via the buttons below the valve test information table. The valve test information table is the interface widget that lists all valves along
        with `Amount Dispensed Per Lick (ul)' and `Testing Opening Time (ms)' columns. Figure \ref{fig:test-buttons} shows the difference 
        between the interface with no buttons selected vs some selected.
    \item \textbf{Start Testing}: From the perspective of the interface, a test can now be started. The user should ensure that the valve 
        cylinders (vials containing stimuli for the valves) are full and all other rig specific guidelines set for the lab are now met. Once 
        the user has ensured that the physical rig is correctly setup for a valve calibration procedure, they can press the big green 
        `Start Testing' button at the bottom of the window.
        \newline
        \newline
        \textbf{NOTE}: \textit{Some} number of valves \textit{above zero} must be selected, or bugs may occur. Ensure that some valves are 
        selected before starting a test procedure.
    \item \textbf{Confirm Test Settings}: Once the user has pressed the green `Start Testing' button, they will see a new pop-up window as 
        shown in Figure \ref{fig:confirm-test}. Review the settings selected using the Valve Test Table, and the entry boxes to ensure the 
        correct settings have been selected. If all setting look okay press `Yes' to begin the procedure. Valves should be heard actuating
        on the rig. 
    \item \textbf{Enter the Amount Dispensed}: In order to understand what the opening time for the valve should be, the actual amount dispensed
        over some number of trials must be found. Find this value either by wighing the item used to collect the dispensed volume or by 
        marking the volume line on the container. Enter this value \textbf{IN MILLILITERS} in the text box pop-up that appears after a test 
        has completed. An example pop-up is shown in Figure \ref{fig:test-pop-up}. Do this for each of the valves that have been tested 
        during this cycle (1 or 2).
        \newline
        \newline
        \textbf{NOTE}: The test procedure has been designed to be flexible and adapt to each specific test. This means that each test may 
        be slightly different from the last. Specifically, the user may select any number of valves to be tested between 1-8. All valves on 
        one side can be tested and none on the other, two on each side, or any number of configurations. 

        Because of this, the user must 
        pay attention and be careful when input pop-ups appear. If there are more than zero valves remaining \textbf{on each side} to be tested,
        there will be \textbf{2 entry boxes} that appear at the end of the test cycle. \textbf{Pay attention} to which valve the program is
        asking the user to enter the dispensed volume for. This is \textit{incredibly easy} to mess up and the test will need to be restarted if 
        this happens. 

        Finally, if the user presses `Cancel' on \textbf{ANY} of the input pop-up windows, the test procedure will be cancelled and will need
        to be restarted. If the red `ABORT TESTING' button is pressed \textit{at any time} during the test procedure, the test will be 
        cancelled. Test settings can then be modified as needed and a test can be restarted. \textit{No program restart} should be necessary 
        to run multiple test procedures.
    \item \textbf{Confirm Duration Changes}: Once all valves selected for a test procedure have been tested, duration changes will be 
        \textit{automatically} calculated. Then, a new pop-up window will appear that will display the change in open duration for each
        valve that was tested. An example of this pop-up window is shown in Figure \ref{fig:results-confirm-popup}. If these changes 
        seem legitimate (no very large jumps or reductions in opening times) confirm them by pressing the green `Confirm Changes' button. 
        Otherwise, press the red `Abort Changes' button and retry the procedure.
\end{enumerate}

\begin{figure}[h!]
    \centering
    \begin{subfigure}[t]{.45\textwidth}
        \centering
        
        \caption{Default State of the Valve Test Window. Buttons not Pressed, all Valves in View in Valve Test Table.}
        \label{fig:unpressed}
    \end{subfigure}
    \hfill
    \begin{subfigure}[t]{.45\textwidth}
        \centering
        
        \caption{Valves 1, 2, 6 Selected. Valve Test Table Shows entries \textit{only} for \textit{these} Valves, Corresponding Buttons 
        Depressed.}
        \label{fig:depressed}
    \end{subfigure}
    \caption{The User will Know a Valve has been Selected when its Corresponding Button has been Depressed (pushed in), and the Valve
    Test Table has been Updated with a row that Includes the Selected Valve.}
    \label{fig:test-buttons}
\end{figure}

\begin{figure}[h!]
        \centering
        
        \caption{The User Must Confirm Test Settings before the Procedure will Begin.}
        \label{fig:confirm-test}
\end{figure}

\begin{figure}[h!]
        \centering
        
        \caption{1 or 2 Input Pop-Up Windows will Appear Depending on Number of Valves Remaing to Test on Each Side.}
        \label{fig:test-pop-up}
\end{figure}

\begin{figure}[h!]
        \centering
        
        \caption{Users can Confirm or Abort Updating the Valve Durations in the `CONFIRM VALVE DURATION CHANGES' Pop-Up Window following a
        Successful Test Procedure.}
        \label{fig:results-confirm-popup}
\end{figure}

\FloatBarrier

\subsection{Manual Valve Duration Adjustment / Duration Profiles}
Manual adjustment of valve timings or changing the selected valve timing `profile' is available by selecting the `Manual Valve Duration 
Override' button just above and to the right of the valve test information table in the `Valve Testing' window. 

\subsubsection{Why was this Necessary?}
Sometimes mistakes are made in the testing procedure. One might overlook an abnormally large adjustment in the automatic calculations that 
could cause issues with proper valve actuation during experiment runtime. Perhaps it is found that a previous duration profile seemed to
work better than the current one for one reason or another. 

Whatever the reason, it is nice to be able to restore things to working order with the press of a single button. This is the purpose of 
valve duration profiles and the manual time adjustment window. This window is pictured below in Figure \ref{fig:manual-window}. 

\begin{figure}[h!]
        \centering
        
        \caption{Users can Override Mistankenly Accepted Automatic Valve Duration Adjustments by Manually Entering New Times in the 
        `Manual Valve Timing Adjustment' window.}
        \label{fig:manual-window}
\end{figure}

\

\subsubsection{Okay, How do I do it? (Setting Valve Duration Profiles)}
Here, users can manually enter different opening times for any of the rig's currently configured 8 valves and save them as the new selected
timings by pressing `Write Timing Changes'. However, most people likely do not have the exact timing for a given valve memorized. To 
aid the user here are different valve timing profiles. To find previously configured or default profiles, click the dropdown menu in the 
top right of this window as shown in Figure \ref{fig:timing-dropdown}.

In this dropdown menu, users have the ability to set durations to one of the following profiles:
\begin{itemize}
    \item \textbf{Default}: Reset all durations back to the default value of 24125 milliseconds by writing the default profile as the new active
        profile. This is a good starting point for calibration on fresh valves.  
    \item \textbf{Last Used}: These timings are the most recently used timings and serve as the active timings for the program. At all times, 
        this profile is the one used during experiments. When new timings are written, they are written into \textit{this} profile.
    \item \textbf{Archive 1}: Archives are used as `back-ups' of older profiles. Anytime a new profile is written (automatic from a valve-test
        or manually) the previous `profile' is set to the newest slot in the archive. The newly created profile is then set as the `Last Used' 
        or current profile. 

        Each time a new archive is added, each archive moves down a slot. For example, if a user writes a new timing 
        profile, the oldest archive profile (`Archive 3') is destroyed. Then the contents of archive 2 move to archive 3 
        (`Archive 2' -> `Archive 3'). Archive 1 then follows the pattern, moving to slot 2 (`Archive 1' -> `Archive 2'). This clears the way
        for the last used profile to be moved to the most recent arhive slot (`Last Used' -> `Archive 1'). Finally, the newly created profile 
        can be set as the active profile (`Last used'). 
    \item \textbf{Archive 2}: Archive 2 is the next archival slot, the second oldest of the archive slots.
    \item \textbf{Archive 3}: Archive 3 is the final archive slot, the oldest of all archives, and is the next profile that will be destroyed 
        upon a new write.
\end{itemize}

\begin{figure}[h!]
    \centering
    
    \caption{Users can Restore old Timings via the Timing Profile Dropdown Selection Menu in the `Manual Valve Timing Adjustment' window.}
    \label{fig:timing-dropdown}
\end{figure}
\FloatBarrier

\clearpage
\subsection{Valve Priming}
\subsubsection{Why is this Useful?}
The final primary feature of the `Valve Testing / Prime Valves' Window is valve `priming'. This is a fancy way of saying "open and close the
valves a bunch of times". The reason this is an included feature is that it was found that simply leaving valves open for an extended period
of time while downstream tubes were full of \textit{only air} (in an attempt to fill them with stimulus) did \textit{not} seem to allow for 
flow to the tip as desired. 

However, it was found that rapidly opening and closing the valves repeatedly \textit{did} effectively allow for flow all the way down to the 
tip of the tubes (albeit slowly).

\subsubsection{Okay, How do I do it? (Priming Valves)}
This process is very similar to the process described in Section \ref{sec:valve-profiles-how-to}. Follow the steps below. This guide assumes
that you have the `Valve Testing' window already open on your display as shown in Figure \ref{fig:test-prime}

\begin{enumerate}
    \item \textbf{Switch to Priming Mode}: First, the user should click the orange button labelled `Switch to Priming Mode' as shown in 
        Figure \ref{fig:test-prime}. This will change the interface to look like Figure \ref{fig:priming-mode}.
            \item \textbf{Enter Valve Acutation Number}: Next, the user should enter how many times the valve should actuate (open and close) before 
        stopping. The use should enter this value in the entry box under the label titled `How Many Times Should the Valve Actuate?'. 
    \item \textbf{Select Valves to Prime}: Finally, the user should select the buttons corresponding to the valves to be primed. 
        To understand what a valve button looks like when it is selected, refer to Figure \ref{fig:test-buttons}.
    \item \textbf{Begin Prime Procedure}: The application is now ready to begin the procedure. Press the orange `Begin Priming' button to 
        begin. 
    \item \textbf{Confirm Prime Settings}: The application will generate a pop-up window similar to that shown in Figure \ref{fig:confirm-test}.
        The user should review the settings in the pop-up window to confirm these are correct. If they are correct, pressing `Yes' will 
        begin the test procedure.
\end{enumerate}
\textbf{Note}: The procedure can be stopped at any time by pressing the yellow `STOP PRIMING' button. The software \textit{does not} need to 
be reset to start a new priming procedure. Once can start and stop as many times as is necessary, changing settings if desired.

After the procedure is complete, check the tubes for the valves just primed. If stimulus has filled the tube to the tip (end nearest spout), 
then the procedure was successful and the tubes are ready for an experiment. If not, repeat the process.

\begin{figure}[h!]
    \centering
    
    \caption{Users can `Prime' Valve by Clicking `Switch to Priming Mode' in the `Valve Test' Window.}
    \label{fig:priming-mode}
\end{figure}
\FloatBarrier

\clearpage
\section{The `Valve Control' Window}
\label{sec:valve-control}
\subsection{What does this Window do?}
The `Valve Control' Window is where users can navigate to manually switch on or off valves for arbitrary lengths of time. They may also manually move the rig door up or
down in this window. The `Valve Control' window is shown in Figure \ref{fig:valve-control-example}.

\subsection{Controlling the Valves}
All valves begin in the off state and can be switched on by pressing the button corresponding to the valve the user would like to open.  
Valves will remain open until user selects this button again. 

This functionality is particularly useful 
for pressurizing valves and quickly running cleaning solution through the stimulus delivery tubes. 
\newline
\newline
\textbf{NOTE}: Be aware and mindful that the valves get \textit{very hot} when left open for long periods of time. 

\subsection{Controlling the Door Motor}
The door motor can be moved down by pressing the green `Move Motor Down' button in this window. The door can be left open or closed as long as the user would like and 
can be moved up and down as many times as necessary. 
\newline
\newline
\textbf{NOTE}: The user should \textit{wait} until the motor movement is \textit{completely finished} before pressing the button again to initiate another movement. 
\newline
\newline
Pressing 
the button before the movement has completed will interfere with the Arduino board's ability to keep track of the current location of the door and will result in the door 
moving too far out of range, potentially \textbf{damaging rig components}. Ensure movements have completed before beginning another.
\newline
\newline
\textbf{IMPORTANT}: The door motor \textbf{must be} in the \textbf{UP} position before starting an experiment. The application assumes this to be the case. If the door is 
left down, similar symptoms as described in the above note will occur. Ensure the motor is in the UP position before leaving this window and beginning an experiment run.

\begin{figure}[h!]
    \centering
    
    \caption{Users can Manually Control Valves as well as the Door Motor in the `Valve Control' Window.}
    \label{fig:valve-control-example}
\end{figure}
\FloatBarrier

\begin{figure}[h!]
    \centering
    
    \caption{Valve Buttons Turn Green on User Press Indicating Valve is Now Open. Motor Button Turns Blue upon User Press to Indicate Door is now Down.}
    \label{fig:valve-control-2}
\end{figure}
\FloatBarrier

\clearpage
\section{The `Program Schedule' Window}
\label{sec:program-schedule}

\subsection{What does this Window do?}
The `Program Schedule' Window allows the user to view one of the primary `dataframe' components where the software stores experiment data. An example of this window 
when populated with data from an upcoming experiment is shown in Figure \ref{fig:prog-sched-ex}.

\begin{figure}[h!]
    \centering
    
    \caption{The Program Schedule Window allows Users to View Basic Current Experiment Data. This Figure Shows the Window Prior to Experiment Beginning, thus the NAN Values
    for Lick Data.}
    \label{fig:prog-sched-ex}
\end{figure}
\FloatBarrier

\clearpage
\subsection{This Window won't Open due to Error... Why? (Experiment Schedule Error)}
The user may see an error when attempting to open this window if they have not yet generated the experiment schedule for the experiment run. The error one may see is shown in
Figure \ref{fig:prog-sched-err}. The steps to generate the schedule are outlined with references to specific sections in Section \ref{sec:start-exp}.

\begin{figure}[h!]
    \centering
    
    \caption{The Program Schedule window will not Open Until the Program Schedule has been Generated for the Experiment.}
    \label{fig:prog-sched-err}
\end{figure}
\FloatBarrier

\subsection{What do All these Fields Mean?}
This section explains each column, its purpose, and the data/units held within the column's rows where applicable. Columns are explained from left to right as they 
appear in the Program Schedule window.
\begin{enumerate}
    \item \textbf{Trial Block}: A trial \textit{block} is a group of trials that contain all possible pairings (unique stimuli pairings) of stimuli delivery during an 
        experiment. 
        
        For example, for an experiment with two stimuli in use for each port, (sucrose, saccarhin Port 1 | sucrose, saccarhin Port 2), each stimulus must be 
        delivered on each port. So there are number of valves / 2 pairings for a trial block. Here there would be 2 trials per block. For the first trial there may be
        Port 1: Sucrose | Port 2: Saccarhin. There must also then be the opposite of this delivery for trial two: Port 1: Saccarhin | Port 2: Sucrose. This example is shown 
        more clearly in Figure \ref{fig:prog-sched-ex}.
    \item \textbf{Trial Number}: Trial number is simply the trial number of the current trial beginning at 1 and ending at total number of trials.
    \item \textbf{Port 1}: Port 1 displays the stimulus to be delivered on Port 1 for the trial in the row.
    \item \textbf{Port 2}: Port 2 displays the stimulus to be delivered on Port 2 for the trial in the row.
    \item \textbf{Port 1 Licks}: Port 1 \textit{Licks} is updated after a trial occurs and shows the number of times Port 1 was licked for this trial.
    \item \textbf{Port 2 Licks}: Port 2 \textit{Licks} is updated after a trial occurs and shows the number of times Port 2 was licked for this trial.
    \item \textbf{ITI}: ITI shows the allocated time for ITI state for a given trial. This time is given in milliseconds. 
    \item \textbf{TTC}: TTC shows the allocated time for a TTC state for a given trial. This time is given in milliseconds. 
    \item \textbf{SAMPLE}: SAMPLE shows the allocated time for a Sample state for a given trial. This time is given in milliseconds. 
    \item \textbf{TTC Actual}: TTC Actual shows the \textit{actual time used} for a TTC state for a given trial. This is necessary because three rat licks will transition the 
        program into a Sample state early, and will not use all allocated TTC time. This time is given in milliseconds. 
\end{enumerate}

\clearpage
\section{The `Valve / Stimuli' Window}
\label{sec:valve-stim-window}
\subsection{What Does this Window Do?}
The `Valve / Stimuli' Window is where users should navigate to label the stimuli that will be delivered for a given valve. This is an important step to generating the program 
schedule as described in Section \ref{sec:start-exp}. The `Valve / Stimuli' window as it will be found on first open is shown in Figure \ref{fig:valve-stim}.

\begin{figure}[h!]
    \centering
    
    \caption{The `Valve / Stimuli' Window is Initially Filled with Default Values Corresponding to the Labelled Valve Number of a Valve.}
    \label{fig:valve-stim}
\end{figure}
\FloatBarrier

\subsection{How Do I Use this Window? (Generating an Experiment Schedule)}
The `Valve / Stimuli' window is where the stimuli schedule is generated for an upcoming experiment. This process will generate not only stimulus lineup for each port 
per trial for the experiment, but also state base interval times (ITI, TTC, etc) and 
the random times to be added to these base times. Assuming that interval times and other experiment configuration variables have been set as desired in the main 
program window (Section \ref{sec:basic-configuration}), the remaining step prior to schedule generation is naming the stimuli for each valve. 

When assigning stimuli names to valves, the user should start at valve one and continue downwards (enter only in new rows, do not enter in column two). This will simplify
the process, as the program will automatically assign names to valves on column two based on names entered in column one. When names have been assigned, users can press the
large green `Generate Schedule' button at the top of the `Valve / Stimuli' window.

If this process is successful, the `Valve / Stimuli' window will disappear, and a new `Program Schedule' window will appear displaying the schedule to be followed for the 
next experiment as shown in Figure \ref{fig:prog-sched-ex}.

\clearpage
\section{The `Event Data' Window}
\label{sec:event-data-window}
The `Event Data' Window shows the user more detailed information about events that occur during an experiment run. While the program schedule shows much of the desired 
information about the experiment to the user, it lacks information like event timestamps, durations, etc. The `Event Data' window fills in these data gaps. 

Details about rat licks as well as door motor movement details are contained in this window. Because two different event types are stored here, some columns may not always 
contain a value. This is discussed in more detail below.

\begin{figure}[h!]
    \centering
    
    \caption{The event data window }
    \label{fig:event-window-ex}
\end{figure}
\FloatBarrier

\subsection{Detailed Column Breakdown}
Here the contents of each column is discussed in detail. This includes general details as well as units of displayed information where applicable.

\begin{enumerate}
    \item \textbf{Trial Number}: This column displays the trial that an event occurred in. 
    \item \textbf{Licked Port}: This column will \textbf{not} always contain a value. It will only be filled if the event being recorded is a rat lick. Motor movement 
        recordings will mark this columns value for this row as `nan'.
    \item \textbf{Event Duration}: This column is used for \textit{both} licks and motor movements. It records the length of time the event occurred in from onset to offset. 
        
        For licks, this is the time difference between the moment the lick beam is broken until the moment it is restored. For door motor movements, it is the time 
        difference between motor movement instruction until the motor reaches the target position. This time is represented in \textbf{milliseconds}.
    \item \textbf{Valve Duration}: Valve duration is only marked for the subset of lick events that occur within the `SAMPLE' state. This is because valves are not 
        opened during `TTC' state. Value stored as nan for licks in `TTC' state or motor movement events. This time is represented in \textbf{milliseconds}.
    \item \textbf{Time Stamp}: This value is the time the event occurred relative to the program start time (t=0) in \textbf{seconds}.
    \item \textbf{Trial Relative Stamp}: This value is the time the event occurred relative to the trial start time. Trial start here is defined as TTC start time, because 
        this is the moment the rat can begin to engage in the trial. This time is represented in \textbf{seconds}.
    \item \textbf{State}: State can hold different values depending on the \textit{type} of event that occurred. Motor movements will state the \textit{type} of motor movement 
        that occurred (MOTOR [UP, DOWN]). Licks will show the program state at the time of the lick (TTC, SAMPLE).
\end{enumerate}
\textbf{NOTE}: The method by which data in this window is refreshed is pressing the `Event Data' button in the main program window. This button serves as the method to 
access the window and update with new information that has occurred. The window will \textbf{NOT} automatically refresh. The user must manually trigger updates via this 
method.

\clearpage
\section{The `Rasterized Data' Window}
\label{sec:rasterized-data-window}
Pressing the `Rasterized Data' button in  the main program window produces two identical raster plots representing the licks per trial per port. This window is useful to 
ensure that reported licks from the Arduino board seem to match with the accepted understanding of how quickly rats can lick maximally. 

In other words, it allows users to
ensure that the data being recorded is accurate, and no `phantom licks' are being recorded due to equipment inadequacies or failures.

In this window, the Y-axis represents trial number, while X-axis values represent the time stamp associated with a given lick.

\begin{figure}[h!]
    \centering
    \begin{subfigure}[t]{.45\textwidth}
        \centering
        
        \caption{Example of Data Filling the Side (Port) 1 Raster Plot.}
        \label{fig:raster-1}
    \end{subfigure}
    \hfill
    \begin{subfigure}[t]{.45\textwidth}
        \centering
        
        \caption{Example of Data Filling the Side (Port) 2 Raster Plot.}
        \label{fig:raster-2}
    \end{subfigure}
    \caption{Raster Plots are Seperated by Port to make Analysis more Straightforward.}
    \label{fig:rasters}
\end{figure}

\end{document}

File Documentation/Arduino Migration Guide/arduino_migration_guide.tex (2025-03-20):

\documentclass{article}

\usepackage{hyperref}
\usepackage{listings}
\usepackage{xcolor}
\usepackage{graphicx}
\usepackage{subcaption}
\usepackage{placeins}
\usepackage{pdfpages}

\graphicspath{{"/home/blake/Pictures/arduino migration guide"}}

\setlength{\parskip}{1em}

\title{\textbf{Photologic Experiment Rig}\\Arduino Migration Guide}
\author{Blake Hourigan}
\date{March 18, 2025}

\lstset{
    basicstyle=\ttfamily\small,
    breaklines=true,
    numbers=left,
    numberstyle=\tiny,
    frame=single,
    keywordstyle=\color{blue},
    commentstyle=\color{gray},
    stringstyle=\color{orange},
}
\lstdefinelanguage{yaml}{
    morekeywords={true,false,null,y,n},      % Add keywords here
    sensitive=false,                        % Case insensitive
    morecomment=[l]{\#},                    % Line comments start with #
    morestring=[b]",                        % Double-quoted strings
    morestring=[b]',                        % Single-quoted strings
}

\begin{document}
\maketitle
\clearpage
\tableofcontents
\clearpage

\section{Why the Migration?}
If you are not interested in why but only \textit{how to perform} the migration, skip to Section \ref{sec:migration}.

When I began working on this project again after about a year-long hiatus, I was struck by various aspects of the program that were much less effiecient than they should be. 
I began work to resolve some of these issues individually on
the two different Arduino boards. I changed data structures, algorithms, moved to simpler structs rather than classes, etc. and I noticed incredible speed-ups in the tasks being 
performed on each board. As things became faster and more efficient, I began to wonder if having \textit{two distinct Arduino boards} was necessary. 

The processor on board is incredibly fast and the tasks being performed are so light that it seemed like overkill to
have two individual boards performing different tasks. Not to mention the overhead of having two separate boards. Handling communication between two different boards meant that code
was required to identify these boards. Often commands needed to be sent to two boards at once rather than combining commands to one board. Furthermore, the Arduino boards needed 
a mechanism to communicate with \textit{each other}. The Laser Arduino needed to somehow communicate the fact that a lick has occurred so that the Motor/Valve Arduino could 
properly respond.

So I became interested in the idea of simplifying this setup. It was just a test at first, but it quickly became clear that this setup would perform similar to, if not better than the 
previous setup. With the added benefit of being able to easily collect and send lick, valve, \textbf{and} motor timestamp data in one place. This allowed for much easier communication 
of this data to the controller program. 

The most difficult part of the process was creating a algorithm for detecting licks, opening valves, and marking closing times while prohibiting 
lick detection until this marking occured. The real complication here was that the algorithm could not \textit{loop or \textbf{block}} the execution of the rest of the code. 
But once this was finished and various pieces of code were optimized
for speed (e.g properly ordering command conditional statements) and testing simulated licks with an onset-to-end duration of as low as 15ms, it was clear that the board could handle these
tasks all together. It is able to record and report these data points, handle door motor operation, valve operation, and lick detection all in the same board. 

This allows for a simpler setup and slightly lower cost of the rig. But the real benefit here is a greater wealth of data and reduced complexity in communication protocols and physical setup. 

For the rest of this article I will detail the steps you must take to migrate your setup from 2 Arduino boards to 1, including hardware and software steps.

\section{The Migration Process}
\label{sec:migration}
I've worked quite hard during this period of development to make distribution of both of the required software packages for the rig as simple and easy as possible. While the Arduino portion of the code is 
slightly more complex, I've tried to detail every step as simply and as verbose as possbile to ensure that anyone can do it. If you follow each step closely, you should be up and running
in no time!

If you are someone who is savvy enough, you may use the KiCAD PCB design file, along with the new Arduino source code files to assist you during this process. These are \textbf{NOT} 
required to complete the migration, but they may be helpful if you get confused or make a misstep along the way. 

If you have downloaded the \href{https://github.com/blakehourigan/Photologic-Experiment-Rig}{Github repository} locally on your computer, the KiCAD project 
file you are looking for will be located at `/Circuitry/Final\_PCB.kicad\_pro'. The Arduino Code is Located at `/Code/Arduino Code'. The root Arduino `.ino' file will be located here, 
with specific function code such as optical sensor pin definition and LED pin definition located under the respective directory inside of the /src directory.

\subsection{Hardware Migration Steps}
First, we will start with the hardware migration steps. Here you are going to eventually remove the Arduino board previously labelled 'Laser Arduino', leaving only the Arduino board previously 
labelled or known as the `Motor Arduino'. If you don't know which is which, identification steps are given below. 

\subsubsection{Identify the `Laser Arduino' Board}
You are going to first identify which Arduino board is the `Laser Arduino' in your setup. If the board is unhelpfully \textbf{not} labelled, it is the board with wires running 
to the PCB (circuit board) whose connectors are labelled 
`Laser\_Power\_Pins1' and `LED\_Logic\_Harness1'. One-by-one, we will migrate every connection here to the board previously known as the `Motor Arduino'.

You \textbf{do not need to remove} the actual connectors on the PCB, that will only complicate the process unnecessarily. 

\subsubsection{Obtain a Small flat-head Screwdriver}
Locate the small flat-head screws that sit atop the Arduino screw terminal boards shown in Figure \ref{fig:ino-terms} that secure the non-connector (loose wire) end to the 
Arduinos. Again, we will remove these wires \textbf{ONE AT A TIME} to simplify this process.

\begin{figure}[h!]
        \centering
        
        \caption{The Arduino Terminal Screws Sit atop the Arduino Board, and Face Away from You if You Look at the Arduino Head On.}
        \label{fig:ino-terms}
\end{figure}
\FloatBarrier

\subsubsection{Remove Unnecessary Connectors}
Now we are going to remove the wires that connect to both Arduino boards that facilitate communication between them. 
\begin{enumerate}
    \item \textbf{Digital Pin 8} - We will begin with digital pin number 8 which functioned as the lick side indicator previously. This pin should be the same on both Arduino boards.
        \begin{enumerate}
            \item \textbf{Locate Digital Pin 8} - Locate the wire attached to digital pin 8 on the \textbf{`Laser Arduino' board}. It is the terminal with the big number 8 on it and the 
                square will be black.
            \item \textbf{Unscrew the Terminal} - Unscrew the terminal with your screwdriver and remove the wire. Follow the wire to the connection on the `Motor Arduino' and repeat 
                the process.
            \item \textbf{Tighten the Terminal Screw} - Tighten the terminal screw back down on both Arduino screw terminal boards. 
        \end{enumerate}
    \item  \textbf{Digital Pin 7} - Next, we will remove digital pin 7 which functioned previously as the lick detected signal. This pin is slightly different because it is 
        \textbf{not the same} on both boards. It is pin 7 on the `Laser Arduino', and is pin number 2 on the `Motor Arduino'.
        \begin{enumerate}
            \item \textbf{Locate Digital Pin 7} - Locate the wire attached to digital pin 7 on the \textbf{`Laser Arduino' board}. It is the terminal with the big number 7 on it and 
                is shaded black.
            \item \textbf{Unscrew the Terminal} - Unscrew the terminal with your screwdriver and remove the wire. Follow the wire to the connection on the `Motor Arduino' and repeat 
                the process.
            \item \textbf{Tighten the Terminal Screw} - Tighten the terminal screw back down on both Arduino screw terminal boards. 
        \end{enumerate}
\end{enumerate}
\subsubsection{Migrating the Remaining PCB Connectors}
Now that we have removed the inter-Arduino communication connections, we just need to migrate the `Laser Arduino' PCB connector wires to the `Motor Arduino'. 
As dicussed above, these include the below connections from the PCB. As before, we will move wires one-by-one starting at the top of the list and moving downwards.
\begin{enumerate}
    \item \textbf{Laser\_Power\_Pins1}\\
        This connector is the easier of the two to migrate. It is just two connectors, 5V and GND. 
        \begin{enumerate}
            \item \textbf{Locate the 5V Wire} - This wire should have red tape wrapped around it and run to a 5V terminal on the `Laser Arduino' board.
            \item \textbf{Remove the Wire from Screw Terminal} - Unscrew the terminal screw that this wire runs to on the `Laser Arduino', and remove the wire from the terminal.
            \item \textbf{Locate a Free (unused) 5V Terminal on `Motor Arduino'} - Find a free 5V slot on the `Motor Arduino' and unscrew the terminal screw. 
            \item \textbf{Secure the Wire into the Terminal} - This step is likely to be one of the more challenging parts of the migration.
                The wire may not reach because it was not originally designed to stretch that far. You may have to play with the location of the `Motor Arduino' board 
                or solder extra wire to get it to reach. 

                \par Once you have situated the boards such that all wires reach their terminals, insert the wire into the 
                open terminal and fasten the wire by tightening the screw until the wire is secure and will not pull from its terminal. 

                \par \textbf{NOTE}: You should pinch the wire with your finger and twist the end around until all 
                of the wire is bundled together cleanly to avoid the wire touching another terminal or not fitting into the terminal well. You should do this every time you 
                insert a wire from this point forward.

            \item \textbf{Locate and Unscrew the Terminal for the GND Wire} - Now, take the other wire from the same connector (the one not wrapped in red tape) and remove it from its screw terminal on the `Laser Arduino'.
            \item \textbf{Locate a Free GND Terminal on the `Motor Arduino'} - Locate a open GND Terminal on the `Motor Arduino', unscrew the terminal, insert the wire, and tighten the screw until 
                the wire is secure and will not pull from its terminal.
        \end{enumerate}

    \item \textbf{LED\_Logic\_Harness1}\\
        Now we are almost done with the hardware migration process! We have just the 4 wires on the LED\_Logic\_Harness1 connector left to go. These wires are easier to 
        differentiate as they are each a different color.
        \begin{enumerate}
            \item \textbf{Locate the ORANGE Wire} - This wire produces the logical output of the optical sensor for spout 1. Looking at the connector plugged into the PCB from which these 
                wires originate, 
                ORANGE lies directly right of YELLOW and above BROWN. \par When I speak of `left', `above', `below', or `right' moving forward, this is what I am referring to.
            \item \textbf{Remove the Wire from Screw Terminal} - Follow the wire to its terminal on the `Laser Arduino', unscrew the terminal screw that this wire runs to, 
                and remove the wire from the terminal.
            \item \textbf{Locate Digital Pin 49 On the `Motor Arduino'} - The pin that we will relocate this wire to is the `Motor Arduino' terminal with the big white number 49 on it. 
            \item \textbf{Secure the ORANGE wire to Digital Pin 49 On the `Motor Arduino'} - Unscrew the screw terminal, insert the wire, and tighten the screw until the wire is secure
                and will not pull from its terminal.
            \item \textbf{Locate the YELLOW Wire} - This wire produces the logical output of the optical sensor for spout 2. It lies directly left of ORANGE and above RED.
            \item \textbf{Remove the Wire from Screw Terminal} - Follow the wire to its terminal on the `Laser Arduino', unscrew the terminal screw that this wire runs to, 
                and remove the wire from the terminal.
            \item \textbf{Locate Digital Pin 47 On the `Motor Arduino'} - The pin that we will relocate this wire to is the `Motor Arduino' terminal with the big white 47 on it. 
            \item \textbf{Secure the YELLOW wire to Digital Pin 47 On the `Motor Arduino'} - Unscrew the screw terminal, insert the wire, and tighten the screw until the wire is secure
                and will not pull from its terminal.
            \item \textbf{Locate the BROWN Wire} - This wire produces the LED `Spout Licked' indicator spout 1. It lies just below the ORANGE wire and and right of RED.
            \item \textbf{Remove the Wire from Screw Terminal} - Follow the wire to its terminal on the `Laser Arduino', unscrew the terminal screw that this wire runs to, 
                and remove the wire from the terminal.
            \item \textbf{Locate Digital Pin 48 On the `Motor Arduino'} - The pin that we will relocate this wire to is the `Motor Arduino' terminal with the big white 48 on it. 
            \item \textbf{Secure the BROWN wire to Digital Pin 48 On the `Motor Arduino'} - Unscrew the screw terminal, insert the wire, and tighten the screw until the wire is secure
                and will not pull from its terminal.
            \item \textbf{Locate the RED Wire} - This wire produces the LED `Spout Licked' indicator spout 2. It lies just below the YELLOW wire and and left of BROWN.
            \item \textbf{Remove the Wire from Screw Terminal} - Follow the wire to its terminal on the `Laser Arduino', unscrew the terminal screw that this wire runs to, 
                and remove the wire from the terminal.
            \item \textbf{Locate Digital Pin 46 On the `Motor Arduino'} - The pin that we will relocate this wire to is the `Motor Arduino' terminal with the big white 46 on it. 
            \item \textbf{Secure the RED wire to Digital Pin 46 On the `Motor Arduino'} - Unscrew the screw terminal, insert the wire, and tighten the screw until the wire is secure
                and will not pull from its terminal.

        \end{enumerate}
\end{enumerate}

\subsubsection{Remove the `Laser Arduino' board from the Setup}
Remove the board which you have removed all connections from, and disconnect its USB cable from the PC. You can set this 
Arduino aside as a backup Arduino board in case anything ever happens to the one currently in use.
\newpage 

\subsection{Software Migration Steps}
Now we have finished the hardware migration portion of the migration! All that is left is installing and uploading the updated software packages! This is a two part process, and should be 
very quick and painless. 
\subsubsection{Installing the New Rig Control Software}

\begin{enumerate}
    \item \textbf{Download the Installer} - First, we will install the new Photologic-Experiment-Rig control software. This is the program that you interact with on the PC when running experiments. 
        \par For this version of the software, 
        a installer program has been created that will do all of the hard and confusing work for you. This installer program can be found 
        \href{https://github.com/blakehourigan/Photologic-Experiment-Rig/releases/tag/v1.0}{on the release page for this version.}  Scroll to the bottom and click on the file named `photologic-rig-setup.exe'. 
        You can see what this download section will look like in Figure \ref{fig:github}. You should notice the installer appear in your active downloads.

        \begin{figure}[h!]
            \centering
            
            \caption{Download the Installer Package Under the Assets Heading on the Github Release Page.}
            \label{fig:github}
        \end{figure}

        \newpage    
    \item \textbf{Open the Installer} - To begin the installation of the program, open the `.exe' file just downloaded. It will look like the image shown in Figures \ref{fig:cont-ide}
        and \ref{fig:cont-no-ide}. If you see a message saying `Windows Protected Your PC', press the text that says `More Info', then click the `Run Anyway button. 
        \par You will need to make a selection here. If you \textbf{DO} currently have the Arduino IDE installed, you can leave this unchecked. If you \textbf{DO NOT}
        have this software installed, you need to check the box and install the software. If you are unsure, check the box to be safe.

        \begin{figure}[h!]
            \centering
            
            \caption{Installing only the Control Software.}
            \label{fig:cont-ide}
        \end{figure}

        \begin{figure}[h!]
            \centering
            
            \caption{Installing the Control Software with the Arduino IDE.}
            \label{fig:cont-no-ide}
        \end{figure}
        \FloatBarrier

    \item \textbf{Click Next and Verify} - Click next, then verify the additional packages to be installed. If you checked the box, the Arduino IDE installer should be listed here
        as in Figure \ref{fig:confirm-install}. If not
        this will just be an empty page.

        \begin{figure}[h!]
            \centering
            
            \caption{Confirm the Packages and Perform Installation.}
            \label{fig:confirm-install}
        \end{figure}
        \FloatBarrier

    \item \textbf{Perform the Installation} - Click install to perform the intallation.

    \item \textbf{Run the Arduino Installer} - When the installer has finished, if you have selected to install the Arduino IDE you will see a screen like that in Figure \ref{fig:ard-install}.
        Make sure you have `Launch Photologic Experiment Rig Control Software' \textbf{unchecked} and run the Arduino IDE setup. Inside of the Arduino installer, you can procede 
        through the installer without changing any defaults. Once the installation is finished, run the Arduino IDE.

        \begin{figure}[h!]
            \centering
            
            \caption{Do NOT Run the Control Software, but DO Run the Arduino Installer.}
            \label{fig:ard-install}
        \end{figure}
        \FloatBarrier

\end{enumerate}

\subsubsection{Installing the Arduino Software Update}
\label{sec:arduino-soft}
Now that you have installed the control software and have the Arduino IDE installed and open on your computer, we will download and install the update to the Arduino board.

\begin{enumerate}
    \item \textbf{Prepare for File Upload} - To upload files to the Arduino board, you will need some `drivers' so that the computer understands how to communicate information to the 
        Arduino. Open the Arduino IDE, connect your Arduino board via its USB cable, and wait for a moment. If you have not opened the IDE before, it will automatically detect that you do not have the packages that you need and will
        prompt you to install them. If these prompts appear, click \textbf{install} on each one of them. 
    \item \textbf{Install Dependencies} - There is one more file that we need to be able to install the update to the board. This is the `AccelStepper' community Arduino library. To install 
        this package, navigate to the `Library Manager' by clicking the third icon down in the left-hand menu in the IDE. This button and window is shown in Figure \ref{fig:ard-lib}. 

        \begin{figure}[h!]
            \centering
            
            \caption{Open the Library Manager to Install Dependencies.}
            \label{fig:ard-lib}
        \end{figure}
        \FloatBarrier
        \par

        Click the search bar of this window, and type `AccelStepper'. You will see an entry at the top as shown in Figure \ref{fig:accel-step}. In the drop-down with numbers in it, left
        of the install button, ensure version number 1.64 is selected. Now click install. This should only take a moment. If the install is successful you should see a message 
        `Installed AccelStepper@1.64.0' in the black terminal window inside the IDE. 
        \begin{figure}[h!]
            \centering
            
            \caption{Install Version 1.64 of the AccelStepper Library.}
            \label{fig:accel-step}
        \end{figure}
        \FloatBarrier
    \item \textbf{Select Your Arduino Board} - If it is not already, plug your Arduino Mega 2560 board into the computer via its USB cable. Once plugged in, click on the drop-down towards 
        the top of your screen titled `Select Board' as shown in Figure \ref{fig:select-board}. Here you should see your board listed. Click on it to select it. Now we are ready to upload code to our board.
        \begin{figure}[h!]
            \centering
            
            \caption{Select Your Arduino in the `Select Board' Menu.}
            \label{fig:select-board}
        \end{figure}
        \FloatBarrier

    \item \textbf{Download the Update} - If you did not do so earlier, download the ArduinoCode.zip file to your computer from the Github release page. This 
        file is listed in the release page `Assets' downloads sections as shown in Figure \ref{fig:github}.
        \newpage 

    \item \textbf{Unzip the Compressed Folder} - Navigate to the folder where you downloaded this file and right click on it. Somewhere in this menu, there will be an option of the form
        `Uncompress Archive', `Unzip archive', `Extract All', or something very similar. Click on this option to produce a regular folder containing the file contents.
    \item \textbf{Open the Update in Arduino IDE} - Navigate back to the open Arduino IDE window, and open the update file by selecting the `file' menu in the top left hand corner, 
        then `open'. Here, navigate to the ArduinoCode folder that you just decompressed, and select the file named `ArduinoCode.ino'. You will see the file content appear in the editor 
        window in the center of your screen. 
    \item \textbf{Upload the Update to the Board} - In the green top bar, hit the middle (second) button with a right arrow in it. This will upload the 
        update to your board. If the update succeeds, you will see a small `Done Uploading.' message in the bottom right hand side of your screen. This is shown in Figure \ref{fig:success}.
        \begin{figure}[h!]
            \centering
            
            \caption{A Successful Upload Shows a `Done Uploading' Notification.}
            \label{fig:success}
        \end{figure}
        \FloatBarrier
\end{enumerate}
That's it! You are done with the migration process from two to one Arduino boards! Now you should test the program to ensure proper functionality with your motor/valves/optical detectors.
This process is detailed below in Section \ref{sec:verifying-func}.

\FloatBarrier

\section{Verifying Functionality}
\label{sec:verifying-func}
At this stage all migration steps are complete. All that we need to do is make sure that everything functions as expected. This guide is going to assume that you have your Arduino board 
plugged into your PC, the door motor is in the `UP' position, and the power supply for the rig is turned on. Please take these steps before following the below guide.

\subsection{Open the Control Software}
Open the control software by beginning to type `Photologic Experiment Rig Control Software' in your start search menu. 
It should quickly appear. It has a cartoon rat icon as its program icon. Click on this entry to open the software.
\subsection{Test that Valves Open and Close Properly}
First, you will need to test that all valves are being recognized. To test that each valve is being recognized properly by the software, follow the steps below:
\begin{enumerate}
    \item Open the valve control window by pressing the `Valve Control' button on the main screen. 
    \item Next, press each button one-by-one and ensure that each LED light corresponding to a valve is properly toggled on and that you hear a 
        valve switch on at the same time. (Figure \ref{fig:valve-cont-wind}.)
        \begin{figure}[h!]
            \centering
            
            \caption{Toggle Valves On and Off by Pressing each Button Once.}
            \label{fig:valve-cont-wind}
        \end{figure}
        \FloatBarrier

    \item If you get this feedback for each valve, and each valve properly turns off again when clicked a second time, valve control is confirmed. 
    \item If not all valves are being recognized, refer to Section \ref{sec:trouble} for troubleshooting details.
\end{enumerate}
\subsection{Test the Door Motor}
Next, we will test to ensure that the door opens and closes as expected. 
\begin{enumerate}
    \item As before, open the `Valve Control' window (Figure \ref{fig:valve-cont-wind}). 
    \item Click the green button that reads `Move Motor Down'. This will send a signal to the Arduino that the 
        motor should move to the down position. 
    \item Once the motor has moved down, wait a moment, then push the blue `Move Motor Up' button.
    \item Repeat the process a few times to ensure no issues arise after a few pushes of the button. 
        \par \textbf{NOTE:} If the button is pushed again \textbf{during} a movement cycle, this will interfere with the 
        Arduinos' sense of where the door is. At this stage you will need to power off the power supply, move the door back up by hand, power on the supply, then reset the Arduino by hitting 
        the physical reset button next to the USB port on the board.
    \item If any errors were experienced, refer to Section \ref{sec:trouble} for troubleshooting details.
\end{enumerate}

\subsection{Test Run an Experiment} 
If the rig has passed all tests thus far, you are ready to test run an experiment. Follow the steps below to test this functionality. This assumes the door is in the `UP' position and
the power supply is on. You will also need a long thin object to run between the optical lick sensors.
\begin{enumerate}
    \item \textbf{Select Your Experiment Settings} - First, select the parameters of the experiment such as ITI TTC, Sample, and random +/- times, along with number of valves in use
        and number of trial blocks. 
    \item Then, label the names of the stimuli inside of your cylinders in the `Valve/Stimuli' window. 
    \item Submit these changes by pressing `Generate Schedule'. 
    \item You can now start an experiment by pressing `Start' in the main program window.
    \item Wait the duration of the first ITI, then during the TTC time run your object between the lick sensor on one side. If all is working you should see the lick 
        indicator LED blinking for that side.
    \item Repeat this 3 times to jump to a Sample time state and observe if valves begin to actuate with lick onset.
    \item Repeat this process for all trials, or if the program is clearly functioning correctly, press `Stop' in the main program window.
    \item If any errors were experienced, refer to Section \ref{sec:trouble} for troubleshooting details.
\end{enumerate}

\subsection{Test a Valve Test Procedure} 
To test the valve testing / calibration functionality, follow the steps listed below. I will assume that you have filled the cylinders with liquid, have left the tops off, and 
have placed cylinders under the side(s) with valves to be tested.
\begin{enumerate}
    \item Press the button on the home screen that reads `Valve Testing / Prime Valves'. 
    \item Enter the amount of microliters that you would like valves to dispense \textbf{on every opening}. Then, enter how many times you would like the valve to actuate. This is 
        \textbf{variable} for convenience, but higher numbers will result in greater accuracy. Calculations will adjust around this number.
    \item Select which valves you would like to test by pressing their respective buttons below the table listing the current durations for each valve. This can be any combination. It
        can be 1 valve or 8, valves on both sides or just one. Any combination except for 0 works.
    \item Now you're ready to start the test procedure, press `Start Testing'.
    \item In the confirmation window, review the valves to be tested and the amount of times each valve will open. If this is okay, press `Yes' to start the procedure.
    \item Wait for the first set of valves to complete. If there are valves remaining to test on each side, both sides will test. If there is only one side with a valve test remaining,
        only that side will be tested.
    \item When the test has ended, you will get either one or two pop-up windows asking the volume dispensed for each valve tested (in mL) in this round of tests. \textbf{PAY ATTENTION TO THE 
        VALVE NUMBER}, it is really easy to mess this up if you look at the \textbf{valve test TABLE} in the main window rather than the pop-up windows specified valve. Find and enter this
        volume and press `OK'. If you press `Cancel' here, the testing sequence will be terminated. You can restart from there if you like or quit testing altogether.
    \item Repeat this process for as many valves as you selected to test.
    \item When all valves have completed, you will see a popup window that displays the previous duration
        and the duration that you are moving to based on testing. If these changes look good, press the 
        green `Confirm Changes' button. If they are not satisfactory, press the red `ABORT CHANGES' button.
    \item The durations that you had saved previously are now saved in the newest archive duration `profile'. These can be found and re-applied if desired in the `Manual 
        Valve Duration Override' window from the main `Valve Testing' window.
    \item If any errors were experienced, refer to Section \ref{sec:trouble} for troubleshooting details.
\end{enumerate}

\subsection{Test a Valve Prime Procedure}
Testing a valve prime procedure is similar to, but even easier than the testing procedure described above. Follow the steps below to verify this functionality.
\begin{enumerate}
    \item As before, open the `Valve Testing / Prime Valves' window, but this time push the orange `Switch to Priming Mode' button at the top of the window.
    \item Enter how many times you would like each valve to actuate.
    \item Select which valves you would like to prime. Again, this can be any combination. It can be 1 valve or 8, valves on both sides or just one. Any combination except for 0 works.
        Push the buttons that correspond to the valves you want to test.
    \item Start the procedure by pressing the orange `Start Priming' button at the bottom of the window.
    \item Confirm the valves to test, and the number of actuations in the pop-up window by pressing `Yes'.
    \item Wait until the prime is finished, or, if you've had enough at any time you can press the yellow `STOP PRIMING' button. You do not have to do anything special to restart the 
        procedure. You can stop and restart as many times as you wish. If you started but found you actually want different settings, that option is available.
    \item Once the valves stop actuating, the procedure is finished and functionality is confirmed.
    \item If any errors were experienced, refer to Section \ref{sec:trouble} for troubleshooting details.
\end{enumerate}

\section{Troubleshooting}
\label{sec:trouble}

\subsection{First, the Golden Rule}
As is true in almost all of electronics, if it is not working, just turning it all the way off and back on again is the best first step in debugging odd infrequent issues. 
This is certainly true here. Control software suddenly not 
working? Close the main window by pressing the red X and try it again. Arduino not opening valves or moving the motor? Press the red restart button on the Arduino, close the control 
software and restart and try it again. None of that worked? Restart the PC and see if that helps. 
\par 
The point is, if you see an error that doesn't come up often, a restart will generally fix it. If problems persist after taking these actions a few times, try the below steps
or get into contact with me at \url{jbhour01@louisville.edu}.

\subsection{General Arduino Troubleshooting Steps}
The most common error that you are likely to experience is an error in communication with the Arduino board for one reason or another. This error will show itself in unresponsive valves, 
door motor, and/or optical detectors. Sometimes the Arduino may get stuck in a loop or have corrupted memory unexpectedly that will cause these or other symptoms. You may get an
`error sending durations', or `error receiving schedule' in the controller program.
\par Other errors you may get are less likely to be resolved by taking the below steps, but you can always try them. 

\begin{itemize}
    \item \textbf{Restart the Arduino Board} - As stated above, usually the easiest and most effective solution is to just restart the Arduino and controller program. Close the controller
        program if it is open, push the red button on the Arduino board, then reopen the controller program.

    \item \textbf{Check the USB Connection between the PC and the Arduino} - It is always a good idea to check the physical connection between the PC and the Arduino. 
        Unplugging the Board at every junction and plugging everything back in may resolve whatever communication issue you are experiencing.

    \item \textbf{Reupload the Arduino Software} - Furthermore, if neither of the previous steps help you, sometimes the board just needs its software reuploaded. Follow the 
        steps described above in section \ref{sec:arduino-soft} to reinstall the software to the board. 

    \item \textbf{Check PCB Connections} - It is always a good idea to make sure that there are NO loose connections on the Arduino board. Pull on them lightly and 
        see if any of them move. If they do, try re-inserting them and tightening the screw. 
    
    \item \textbf{Try the Other Arduino} - Finally, if you problem is Arduino related it could be your individual board. You can remove the terminal screw `hat' that sits on top of the 
        Arduino board, transfer it to another Arduino Mega 2560 and upload the software to it (Section \ref{sec:arduino-soft}). 
\end{itemize}

If none of these issues fix your Arduino problem, email be at \url{jbhour01@louisville.edu}.

\subsection{What to do if Valves do not Open as Expected?}
If you find after testing each valve individually that the valves (particularly side two) are not opening as expected, and the Arduino troubleshooting steps did not help you 
please send the following information along with a problem desciption to my email.

\begin{itemize}
    \item Document which (if any) valves do open correctly when you press the buttons in the control software.
    \item Photograph the connections between the PCB and the Arduino board. The connection I am most interested in here will be the largest connector on the board with 16 connetions. If 
        you could get a good photograph of this setup and what pins each wire runs to on the screw terminal board, this should be a simple issue to debug quickly.
    \item Logfiles. Your logfiles will be in your documents folder, under `Photologic-Experiment-Rig-Files'. Please locate the most recent logfiles and attach them to the email.
\end{itemize}

\subsection{What to do if the Door Motor does not Move as Expected?}
If you find that the door motor does not work at all, but other functions such as valve opening DO work, first make certain that there
are \textbf{NO} loose connections on the Arduino board. Pull on them lightly and see if any of them move. If they do, try re-inserting them and tightening the screw. 

If none of 
these things or the above Arduino troubleshooting steps help and you've restarted the program a few times to no avail, email me at \url{jbhour01@louisville.edu}. 
I will look into the issue and try to get back to you with a fix as quickly as possible.

\subsection{Other Issues} 
For other issues that persist despite your best efforts to troubleshoot, please email me at \url{jbhour01@louisville.edu}. 
I will look into the issue and try to get back to you with a fix as quickly as possible.

\newpage
\section{In Closing}
I hope that this guide makes the transition as smooth as possible. I tested this at my house and everything worked on multiple PCs, so I hope this continues to your lab. I am 
currently working on a full user guide that will teach you how to use every part of the software in detail. I am also working towards code documentation that will make 
future development easier. 
\par Any questions 
you may have would be best asked in the near future because everything about this project is fresh in my mind right now. Once again, please send any questions or 
concerns that you have to 
my email at \url{jbhour01@louisville.edu}. 

Blake Hourigan

\end{document}

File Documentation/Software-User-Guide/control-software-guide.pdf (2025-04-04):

## Photologic Experiment Rig Control Software User Guide

Blake Hourigan

March 30, 2025

1

## Contents

1 Introduction | 4
2 Installing the Software | 4
3 The Main Control Window | 12
4 ‘Valve Testing / Prime Valves’ Window | 22

4.1 Valve Open Duration Calibration (Running a Valve Test) . . . . 23

4.2.2 Okay, How do I do it? (Setting Valve Duration Profiles) . 28

2

5 The ‘Valve Control’ Window | 32
6 The ‘Program Schedule’ Window | 34

6.2 This Window won’t Open due to Error... Why? (Experiment

7 The ‘Valve / Stimuli’ Window | 37

7.2 How Do I Use this Window? (Generating an Experiment Schedule) 37

8 The ‘Event Data’ Window | 38
9 The ‘Rasterized Data’ Window | 40

3

## 1 Introduction

This guide provides simple overviews of included features in the Photologic-Experiment-Rig control software. It also explains the specifics of these features and how to use them. Some features may not have robust explanations within the software as to what type/unit of value goes in a text box, what a certain value displayed in a menu means, among other various confusions.

This guide is intended to make up for areas of the program that may lack in clarity. Each primary user interface window has its own section here that you can jump to using the table of contents.

## 2 Installing the Software

An installation guide for all software required to get the rig up and running has been written in another article. For convenience this is provided in the pages that follow. Because the guide included is a PDF in itself, the page numbers will appear out of order until the software guide is complete.

4

## 2.2 Software Migration Steps

Now we have finished the hardware migration portion of the migration! All that is left is installing and uploading the updated software packages! This is a two part process, and should be very quick and painless.

### 2.2.1 Installing the New Rig Control Software

1. Download the Installer - First, we will install the new Photologic-Experiment-Rig control software. This is the program that you interact with on the PC when running experiments.
For this version of the software, a installer program has been created that will do all of the hard and confusing work for you. This installer program can be found on the release page for this version. Scroll to the bottom and click on the file named ‘photologic-rig-setup.exe’. You can see what this download section will look like in Figure 2. You should notice the installer appear in your active downloads.

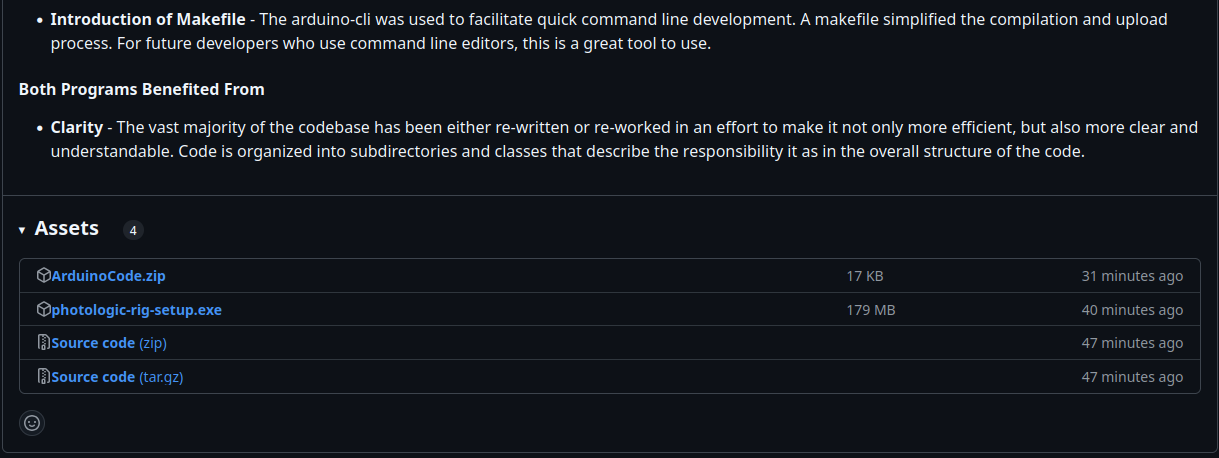
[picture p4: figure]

Figure 2: Download the Installer Package Under the Assets Heading on the Github Release Page.

10

2. Open the Installer - To begin the installation of the program, open the ‘.exe’ file just downloaded. It will look like the image shown in Figures 3 and 4. If you see a message saying ‘Windows Protected Your PC’, press the text that says ‘More Info’, then click the ‘Run Anyway button.
You will need to make a selection here. If you DO currently have the Arduino IDE installed, you can leave this unchecked. If you DO NOT have this software installed, you need to check the box and install the software. If you are unsure, check the box to be safe.

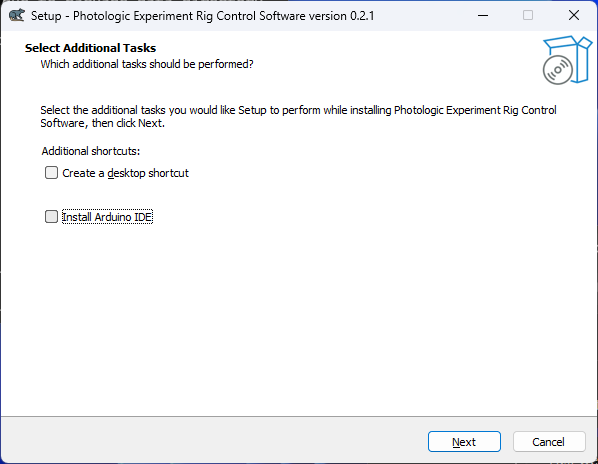
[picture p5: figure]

Figure 3: Installing only the Control Software.

11

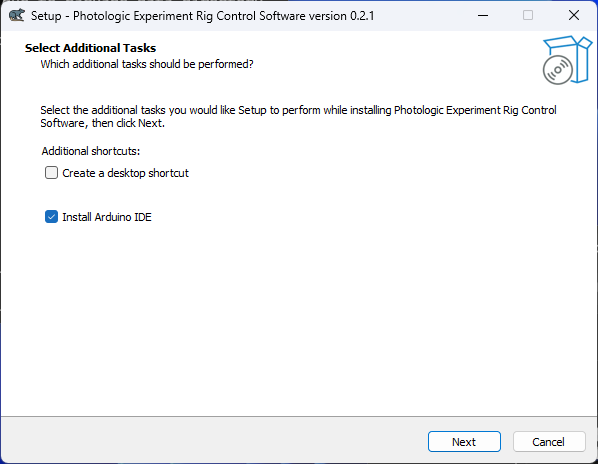
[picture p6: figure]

Figure 4: Installing the Control Software with the Arduino IDE.

3. Click Next and Verify - Click next, then verify the additional packages to be installed. If you checked the box, the Arduino IDE installer should be listed here as in Figure 5. If not this will just be an empty page.

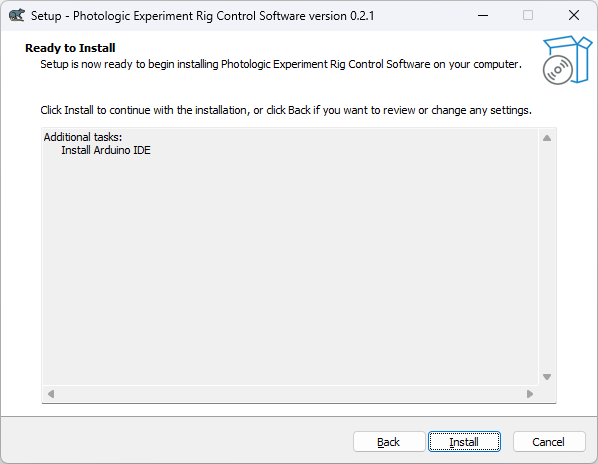
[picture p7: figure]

Figure 5: Confirm the Packages and Perform Installation.

4. Perform the Installation - Click install to perform the intallation.
5. Run the Arduino Installer - When the installer has finished, if you

12 have selected to install the Arduino IDE you will see a screen like that in Figure 6. Make sure you have ‘Launch Photologic Experiment Rig Control Software’ unchecked and run the Arduino IDE setup. Inside of the Arduino installer, you can procede through the installer without changing any defaults. Once the installation is finished, run the Arduino IDE.

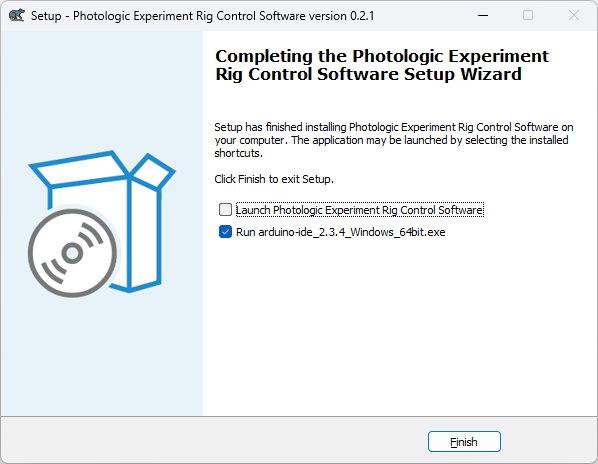
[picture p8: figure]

Figure 6: Do NOT Run the Control Software, but DO Run the Arduino Installer.

### 2.2.2 Installing the Arduino Software Update

Now that you have installed the control software and have the Arduino IDE installed and open on your computer, we will download and install the update to the Arduino board.

1. Prepare for File Upload - To upload files to the Arduino board, you will need some ‘drivers’ so that the computer understands how to communicate information to the Arduino. Open the Arduino IDE, connect your Arduino board via its USB cable, and wait for a moment. If you have not opened the IDE before, it will automatically detect that you do not have the packages that you need and will prompt you to install them. If these prompts appear, click install on each one of them.
2. Install Dependencies - There is one more file that we need to be able to install the update to the board. This is the ‘AccelStepper’ community Arduino library. To install this package, navigate to the ‘Library Manager’

13 by clicking the third icon down in the left-hand menu in the IDE. This button and window is shown in Figure 7.

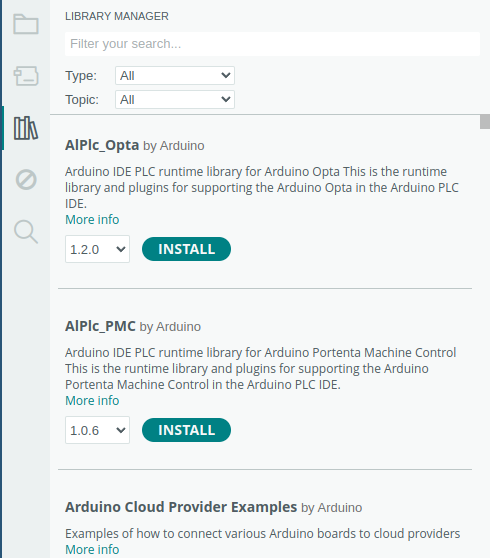
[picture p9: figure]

Figure 7: Open the Library Manager to Install Dependencies.

Click the search bar of this window, and type ‘AccelStepper’. You will see an entry at the top as shown in Figure 8. In the drop-down with numbers in it, left of the install button, ensure version number 1.64 is selected. Now click install. This should only take a moment. If the install is successful you should see a message ‘Installed AccelStepper@1.64.0’ in the black terminal window inside the IDE.

14

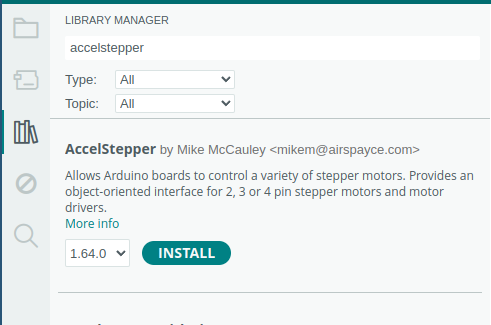
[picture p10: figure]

Figure 8: Install Version 1.64 of the AccelStepper Library.

3. Select Your Arduino Board - If it is not already, plug your Arduino Mega 2560 board into the computer via its USB cable. Once plugged in, click on the drop-down towards the top of your screen titled ‘Select Board’ as shown in Figure 9. Here you should see your board listed. Click on it to select it. Now we are ready to upload code to our board.

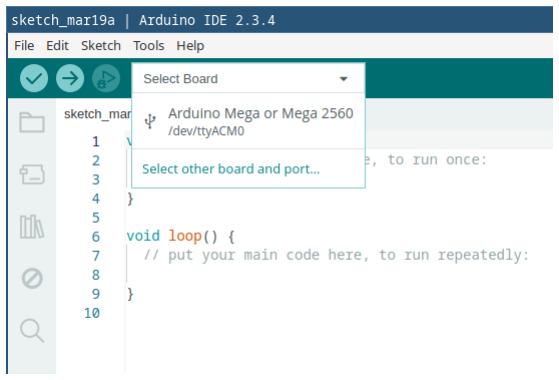
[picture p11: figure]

Figure 9: Select Your Arduino in the ‘Select Board’ Menu.

4. Download the Update - If you did not do so earlier, download the ArduinoCode.zip file to your computer from the Github release page. This file is listed in the release page ‘Assets’ downloads sections as shown in Figure 2.

15

5. Unzip the Compressed Folder - Navigate to the folder where you downloaded this file and right click on it. Somewhere in this menu, there will be an option of the form ‘Uncompress Archive’, ‘Unzip archive’, ‘Extract All’, or something very similar. Click on this option to produce a regular folder containing the file contents.
6. Open the Update in Arduino IDE - Navigate back to the open Arduino IDE window, and open the update file by selecting the ‘file’ menu in the top left hand corner, then ‘open’. Here, navigate to the ArduinoCode folder that you just decompressed, and select the file named ‘ArduinoCode.ino’. You will see the file content appear in the editor window in the center of your screen.
7. Upload the Update to the Board - In the green top bar, hit the middle (second) button with a right arrow in it. This will upload the update to your board. If the update succeeds, you will see a small ‘Done Uploading.’ message in the bottom right hand side of your screen. This is shown in Figure 10.

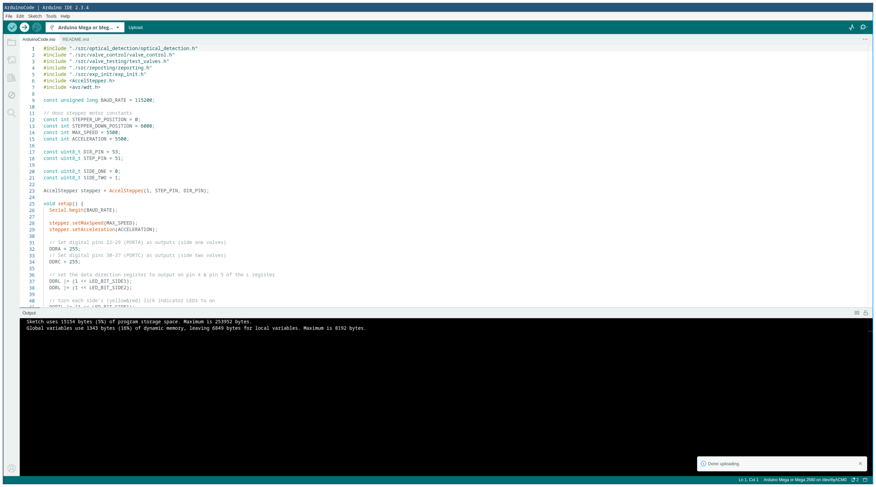
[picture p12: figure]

Figure 10: A Successful Upload Shows a ‘Done Uploading’ Notification.

That’s it! You are done with the migration process from two to one Arduino boards! Now you should test the program to ensure proper functionality with your motor/valves/optical detectors. This process is detailed below in Section 3.

16

## 3 The Main Control Window

The ‘Main Control Window’ refers to the user interface window that appears first upon application startup. This window is the heart of the program and is where much of the required experiment configuration will take place. This window is shown below in Figure 1.

This window can be broken down into 5 primary sub-sections, and as such, this section of the guide is broken down into sub-sections that reflect this layout.

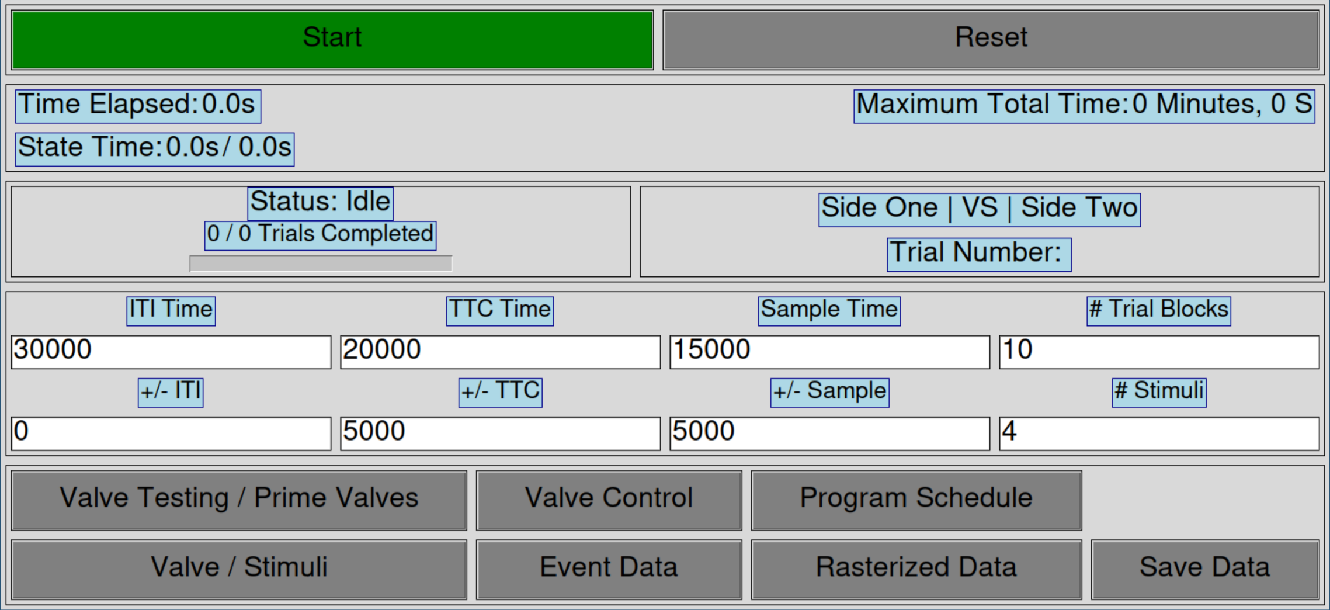
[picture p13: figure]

Figure 1: The ‘Main Control Window’ is the root of all application logic and sub-windows. It allows for navigation to these sub-windows, and allows users to configure and begin experiments.

12

### 3.1 Row 1 - Start and Reset

Row 1 contains two of the most important buttons in the application interface. Start/Stop allows a user to command the program to begin or terminate an experiment depending on current state. Reset allows the user to clear all existing experiment data and ready the application for a new experiment run.

### 3.1.1 Start and Stop (an Experiment)

The start button is important because it allows the user to begin or end an experiment. Before the user can begin an experiment, the experiment must be fully configured. This means that all of the following steps must be completed to continue:

1. Base state interval times (ITI, TTC, Sample, etc.), random interval times (+/- ITI, +/- TTC, +/- Sample, etc.) and other configuration variables (# Trial Blocks, # Stimuli) must be defined. Discussed in Section 3.4.
2. All valves must be configured with corresponding stimulus names in the ‘Valve / Stimuli’ window. Discussed in depth in Section 7.
3. The program schedule must be generated. Discussed in depth in Section 7.

Once all of these requirements have been fulfilled the user can begin an experiment run. If a step has been missed, or something has gone wrong, the user may see a warning message such as the one in Figure 2a. This indicates that the program stimuli schedule has not yet been generated, and that the user should re-visit the ’Valve / Stimuli’ window (Section 7) to attempt a proper schedule generation.

If a experiment run has been started, the ‘Start’ button will be changed to a stop button as shown in Figure 2b. Pressing this button will terminate the experiment early. This will begin the standard termination process. This includes:

- Halting program execution. No further experiment operations will be taken. Door will not close, program state will be switched to "IDLE".
- Terminating the connection to the Arudino board .
- Preparing all accumulated data to be saved.
- The user will be prompted to optionally save this data via a pop-up window in a location of their chosing.

13

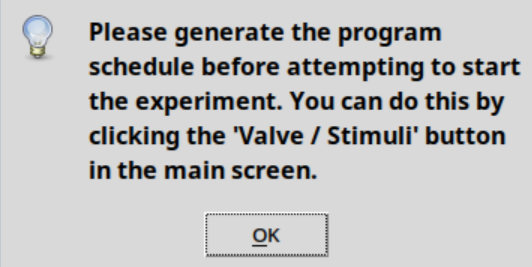
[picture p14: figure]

(a) Without an Experiment Schedule, the program isn’t sure what to do. You must generate a schedule following the steps above to run an experiment.
(b) Start Button is Converted to Stop Button on Experiment Start.

Figure 2

### 3.1.2 Reset (Preparing for a New Experiment)

The other primary button in this row of the main window is the ‘Reset’ button. This button is important because it is required after running an experiment that the user takes either of the two following actions:

1. Presses the gray ’Reset’ button in the main program window.
2. Use the familiar red Windows ‘X’ in the corner of the main application window to close the application session and manually restart by clicking the ‘Photologic-Experiment-Rig’ control software icon on the desktop or in the taskbar. This is the icon with a cartoon rat on it.

Both of these actions perform the same effective operation which is to clear the data from the previous experiment and get the program ready for a new experiment. To reiterate, pressing ‘Reset’ will destroy all experiment data accumulated if the user has not saved this data by pressing the ‘Save Data’ button in the fifth row of the main experiment window since the last experiment was run. This means the user should be very careful when pressing this button.

It is for this reason that when a user presses the Reset button, a warning will be displayed as shown in Figure 3. If the user selects ‘Yes’ in this popup window all data will be destroyed and all windows will be closed, then the main program window will re-open automatically, ready for a new experiment.

NOTE: This action cannot be performed unless an experiment is not currently running. Otherwise, you must stop the current experiment and then reset the application.

14

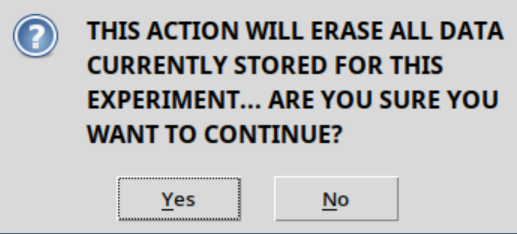
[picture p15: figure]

Figure 3: User must Confirm a Reset Action before it will Execute to Prevent Accidental Loss of Data.

### 3.2 Row 2 - Program Timers

The second row of the main program window features three timers that inform the user of the following pieces of information:

1. Time Elapsed: How long the program has been running in total
2. State Time: How long the program has been in the current state (ITI, TTC, DOOR OPEN, etc.).
3. Maximum Total Time: Maximum amount of time the program can possibly run.

These timers all begin at zero until the program schedule has been generated (discussed in Section 7) and the user presses the ‘Start’ button in the main experiment window. Once an experiment has begun, this row will be populated to reflect the real values that belong here as shown in Figure 4.

Figure 4

15

### 3.2.1 Time Elapsed

This timer is the primary timer for the currently running experiment. This timer shows the time elapsed since the moment the user pressed the start button. It
follows a format of ‘SS | MM:SS’, where the ‘SS’ before the format separator
(‘|’) is the total seconds elapsed since program start time.

Because this is a bit unwieldy and perhaps unhelpful, the information following the separator ‘|’ shows the same figure converted to minutes and seconds. This allows for an easier understanding at a glance of total experiment time elapsed.

### 3.2.2 State Time

The ‘State Time’ timer keeps track not only of the amount of state time that has elapsed since the state began, but also the maximum time it could possible consume. The timer follows the format of ‘ELAPSED TIME / TOTAL AVAILABLE TIME’.

The only time throughout an experiment when the ‘TOTAL TIME’ figure may not be met is during the ‘TTC’ time. This time can be cut short if the rat chooses to engage in the trial. Thus the state timer may end before reaching ‘TOTAL TIME’.

### 3.2.3 Maximum Total Time

The ‘Maximum Total Time’ timer is included as a convenience function that gives the user a general idea of how long an experiment could possibly take. It is almost certain to be inaccurate and over-estimate the amount of time an experiment will take, because it calculates this value by summing all base interval values and random interval values together.

This means that the program assumes that all intervals — including TTC intervals — will use all of their allocated time. This is very unlikely to be true, as the rat is likely to engage in at least some trials. However, it still gives a general idea of the length of time an experiment may take.

16

### 3.3 Row 3 - Status Indicators

Row 3 contains many different experiment status indicators that inform the user of the current values of important trial variables. These include:

- Status (Program State): This indicator informs the user of the current program state ("IDLE", "ITI", "TTC", etc.)
- Trials Completed (Current Trial/Total Trials): Displays the current trial and total trials for this experiment. Includes a progress indicator to show experiment progress at a glance.
- Side One: {Stimulus} |VS| Side Two: {Stimulus}: Current Stimulus Delivery per Port (Side): Inform user which stimulus is being delivered on each port (side) for the current trial.

Examples of what these indicators look like during an experiment run are shown in Figure 5.

Figure 5: Status Indicators Aid the User by Informing them of the Current State of Experiment Variables.

17

### 3.4 Row 4 - Configuring the Experiment

Row 4 is one of the rows in the main window that the user will interact with the most. This row is where the user enters any desired configuration changes for an upcoming experiment. This row and the contained entry widgets are shown in Figure 6.

The primary experiment variables that may change from experiment to experiment are the base state intervals (ITI, TTC, Sample), random state intervals (+/- ITI, +/-, TTC, etc), ‘# Trial Blocks’ (number of times each possible stimulus pairing should be delivered), and ‘# Stimuli’ (number of valves in use).

Figure 6: The Entry Widgets in the Main Window Allow the User to Modify Default Experiment Variables.

These variables should be changed before the schedule is generated for the experiment.

NOTE: All time-related values (interval times) must be given in milliseconds. For example, 30 seconds should be entered in as 30000 milliseconds.

Ensure that no entry boxes are left empty before generating the schedule. Each box needs to contain some positive integer to correctly generate the experiment schedule.

18

### 3.4.1 Changing Default Values

If the default values need to be modified, this requires a change in the Python codebase. This is an involved process because new versions of the program need to be compiled and built into a new installer. (https://gist.github.com/blakehourigan/5e176f2600446a793547babff372299c)

Default values are defined in the GitHub repository directory in the file found at subdirectory ‘/Code/Photologic Rig Main Application Code/src/models/experiment_process_data.py’ under variables named self.interval_vars, and self.exp_var_entries.

This code is shown in Listing 1. Defaults can be changed here, but again a new program build and installer must be created and installed onto the user’s machine. Users may need to ask the lab tech for assistance in this process.

1 | self . interval_vars : dict [str , int] = {
2 | " ITI_var ": 30000 ,
3 | " TTC_var ": 20000 ,
4 | " sample_var ": 15000 ,
5 | " ITI_random_entry ": 0,
6 | " TTC_random_entry ": 5000 ,
7 | " sample_random_entry ": 5000 ,
8 | }
9 | self . exp_var_entries : dict [str , int ] = {
10 | " Num Trial Blocks ": 10 ,
11 | " Num Stimuli ": 4 ,
12 | " Num Trials ": 0,
13 | }

Listing 1: Default values can be seen Above. Time-Related Interval Values are Separated from Other Values like Number of Trials.

19

### 3.5 Row 5 - Accessing Other Control Windows

Row 5 of the main program window contains 7 gray buttons that allow for navigation to other important experiment control windows. (Figure 7)

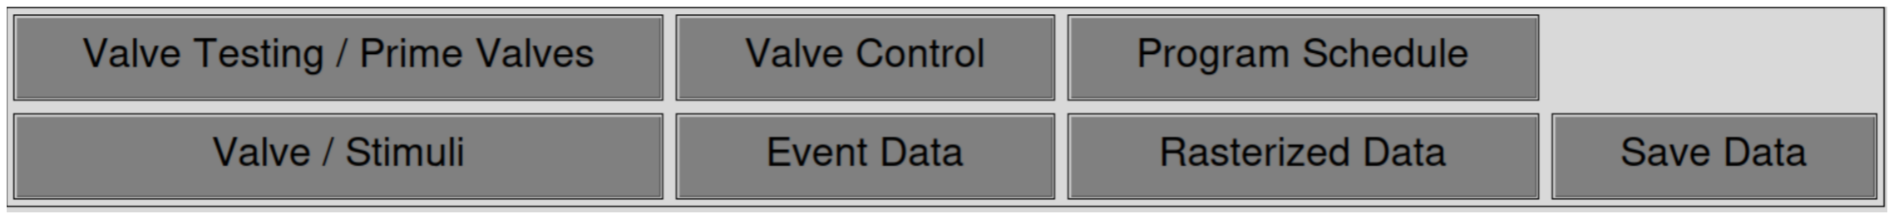
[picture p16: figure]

Figure 7: The Buttons in Row 5 Allow for Navigation to Other Experiment Windows.

Descriptions of buttons and their functions will begin on the first row and column of this section. Each button in a row will be described, then the next row will be described.

1. Valve Testing / Prime Valves: This button allows for navigation to the ‘Valve Testing / Prime Valves’ window. A user would navigate here if they desired calibrating valve opening durations via the automatic testing procedure or if they desired to ‘Prime’ the valves prior to an experimnet run. This window is discussed in depth in Section 4.
2. Valve Control: This button allows for navigation to the ‘Valve Control’ window. A user would navigate here if they desired opening or closing valves for arbitrary lengths of time. This window also allows for the manual toggling of the rig’s door motor to the up or down position for arbitrary lengths of time. This window is discussed in depth in Section 5.
3. Program Schedule: This button allows for navigation to the ‘Program Schedule’ window. This is where the user would find most experiment data including:
- Trial block numbers.
- Trial numbers.
- Licks-per-port for a trial.
- Stimulus delivered on each side for a trial.
- ITI, TTC, Sample times for a trial.

This window is discussed in depth in Section 6.

4. Valve / Stimuli: This button allows for navigation to the ‘Valve / Stimuli’ window. This is where the user navigates to assign stimuli names to specific valves for the experiment. This is required to generate the experiment schedule. This window and associated functions are discussed in depth in Section 7.

20

5. Event Data: This button allows for navigation to the ‘Event Data’ window. This is where all data not included in the ‘Program Schedule’ window is found. A user might navigate here to view detailed data about specific events that take place during the program like licks or door motor movements. This window is discussed in depth in Section 8.
6. Rasterized Data: This button allows for navigation to the ‘Rasterized Data’ window. A user might navigate here to view lick data per trial in a raster plot. This window is discussed in depth in Section 9.
7. Save Data: This button is used to save all currently held data into 2 separate excel spreadsheet files. Data in the program is split into 2 primary ‘DataFrames’. These DataFrames include the ‘Program Schedule DataFrame’ and the ‘Event Dataframe’. The data stored in each frame is as described previously for each respective window corresponding to these DataFrames.

21

## 4 ‘Valve Testing / Prime Valves’ Window

This window is where the user would navigate for valve opening duration calibration or valve ‘priming’ before a experiment run. The ‘Valve Testing / Prime Valves’ window is shown below in Figure 8.

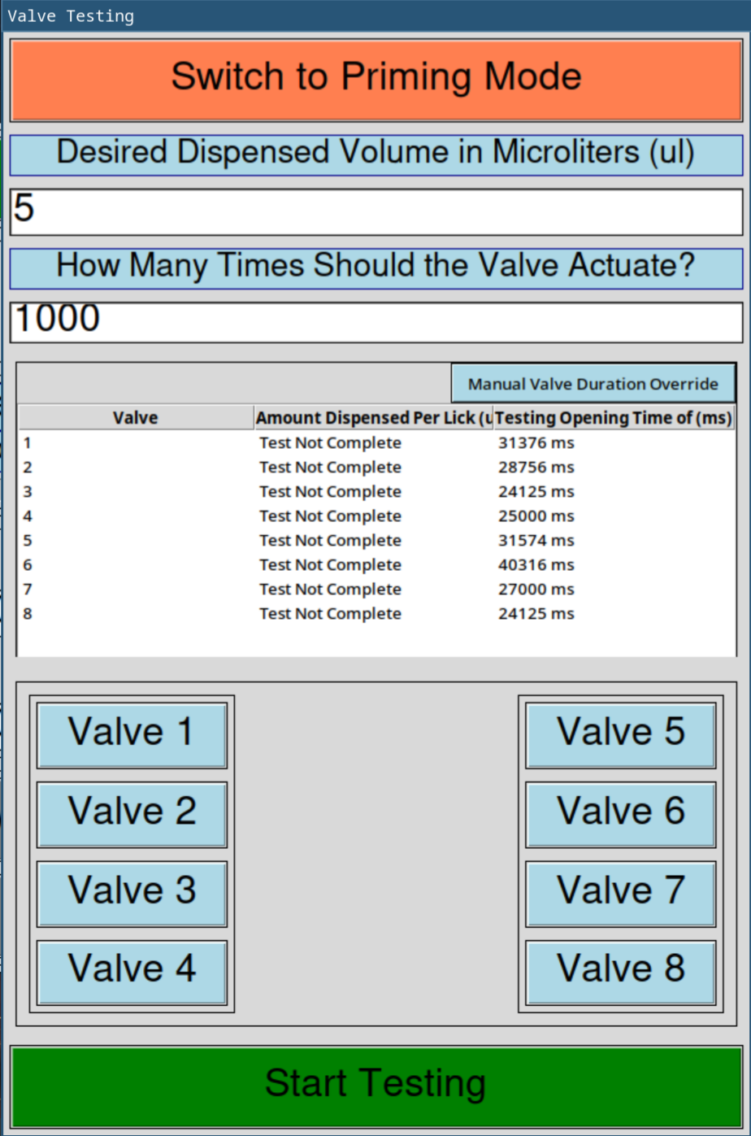
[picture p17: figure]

Figure 8: The ‘Valve Testing / Prime Valves’ Window opens in Testing Mode upon First Button Press.

22

### 4.1 Valve Open Duration Calibration (Running a Valve

Test)

This window opens in ‘Testing’ mode by default. A user can be sure that they are in test mode if the large orange ‘Switch to Priming Mode’ button is in view at the top of the window.

In this window a user will notice several interface components that are critical to a successful valve calibration. Calibration is important to run often to ensure that each valve is delivering the proper amount of stimulus on each valve in use during an experiment. The process of running a valve test procedure is described below.

1. Enter Desired Amount of Stimulus Per Lick: First, the user should enter how much liquid that is desired each time the valve opens in the entry box just below the label ‘Desired Dispensed Volume in Microliters (ul)’. The default value for this entry is 5 microliters.
2. Enter Number of Valve Actuations: Then, enter the number of times a valve should open and close for each test in the entry box just below the label ‘How Many Times Should the Valve Actuate?’.

The default value for this entry is 1000 and is a good starting point for testing. This attribute of the procedure is variable in the event that a user wants to change this value, and new duration calculations will adjust to the value input in this field. However, higher numbers will yield more accuration calculations.

3. Select Valves to be Tested: Next, the user should select the valves to be tested during this procedure. This is done by selecting valves via the buttons below the valve test information table. The valve test information table is the interface widget that lists all valves along with ‘Amount Dispensed Per Lick (ul)’ and ‘Testing Opening Time (ms)’ columns. Figure 9 shows the difference between the interface with no buttons selected vs some selected.
4. Start Testing: From the perspective of the interface, a test can now be started. The user should ensure that the valve cylinders (vials containing stimuli for the valves) are full and all other rig specific guidelines set for the lab are now met. Once the user has ensured that the physical rig is correctly setup for a valve calibration procedure, they can press the big green ‘Start Testing’ button at the bottom of the window.

NOTE: Some number of valves above zero must be selected, or bugs may occur. Ensure that some valves are selected before starting a test procedure.

23

5. Confirm Test Settings: Once the user has pressed the green ‘Start Testing’ button, they will see a new pop-up window as shown in Figure
10. Review the settings selected using the Valve Test Table, and the entry boxes to ensure the correct settings have been selected. If all setting look okay press ‘Yes’ to begin the procedure. Valves should be heard actuating on the rig.
6. Enter the Amount Dispensed: In order to understand what the opening time for the valve should be, the actual amount dispensed over some number of trials must be found. Find this value either by wighing the item used to collect the dispensed volume or by marking the volume line on the container. Enter this value IN MILLILITERS in the text box pop-up that appears after a test has completed. An example pop-up is shown in Figure 11. Do this for each of the valves that have been tested during this cycle (1 or 2).

NOTE: The test procedure has been designed to be flexible and adapt to each specific test. This means that each test may be slightly different from the last. Specifically, the user may select any number of valves to be tested between 1-8. All valves on one side can be tested and none on the other, two on each side, or any number of configurations.

Because of this, the user must pay attention and be careful when input pop-ups appear. If there are more than zero valves remaining on each side to be tested, there will be 2 entry boxes that appear at the end of the test cycle. Pay attention to which valve the program is asking the user to enter the dispensed volume for. This is incredibly easy to mess up and the test will need to be restarted if this happens.

Finally, if the user presses ‘Cancel’ on ANY of the input pop-up windows, the test procedure will be cancelled and will need to be restarted. If the red ‘ABORT TESTING’ button is pressed at any time during the test procedure, the test will be cancelled. Test settings can then be modified as needed and a test can be restarted. No program restart should be necessary to run multiple test procedures.

7. Confirm Duration Changes: Once all valves selected for a test procedure have been tested, duration changes will be automatically calculated. Then, a new pop-up window will appear that will display the change in open duration for each valve that was tested. An example of this popup window is shown in Figure 12. If these changes seem legitimate (no very large jumps or reductions in opening times) confirm them by pressing the green ‘Confirm Changes’ button. Otherwise, press the red ‘Abort Changes’ button and retry the procedure.

24

(a) Default State of the Valve Test Window. Buttons not Pressed, all Valves in View in Valve Test Table.

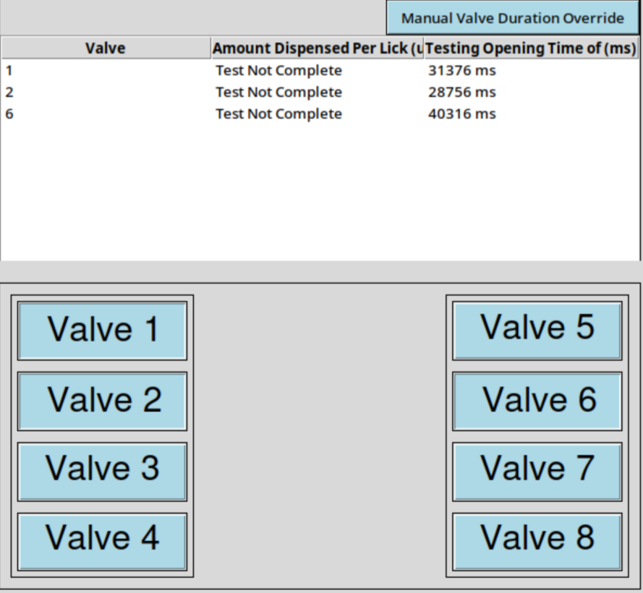
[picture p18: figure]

(b) Valves 1, 2, 6 Selected. Valve Test Table Shows entries only for these Valves, Corresponding Buttons Depressed.

Figure 9: The User will Know a Valve has been Selected when its Corresponding Button has been Depressed (pushed in), and the Valve Test Table has been Updated with a row that Includes the Selected Valve.

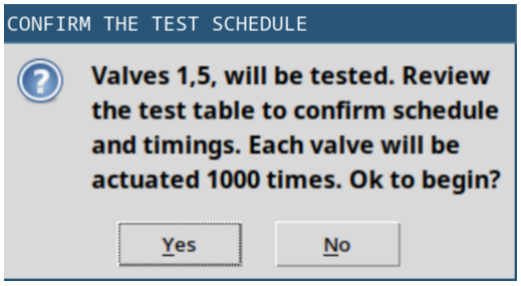
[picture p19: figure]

Figure 10: The User Must Confirm Test Settings before the Procedure will Begin.

25

Figure 11: 1 or 2 Input Pop-Up Windows will Appear Depending on Number of Valves Remaing to Test on Each Side.

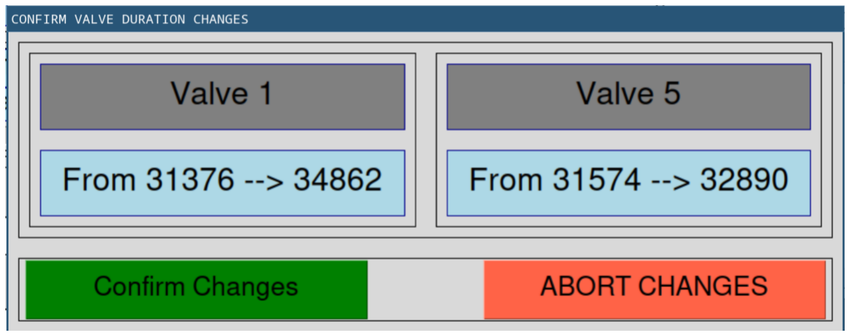
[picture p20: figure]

Figure 12: Users can Confirm or Abort Updating the Valve Durations in the ‘CONFIRM VALVE DURATION CHANGES’ Pop-Up Window following a Successful Test Procedure.

26

### 4.2 Manual Valve Duration Adjustment / Duration Pro-

files

Manual adjustment of valve timings or changing the selected valve timing ‘profile’ is available by selecting the ‘Manual Valve Duration Override’ button just above and to the right of the valve test information table in the ‘Valve Testing’ window.

### 4.2.1 Why was this Necessary?

Sometimes mistakes are made in the testing procedure. One might overlook an abnormally large adjustment in the automatic calculations that could cause issues with proper valve actuation during experiment runtime. Perhaps it is found that a previous duration profile seemed to work better than the current one for one reason or another.

Whatever the reason, it is nice to be able to restore things to working order with the press of a single button. This is the purpose of valve duration profiles and the manual time adjustment window. This window is pictured below in Figure 13.

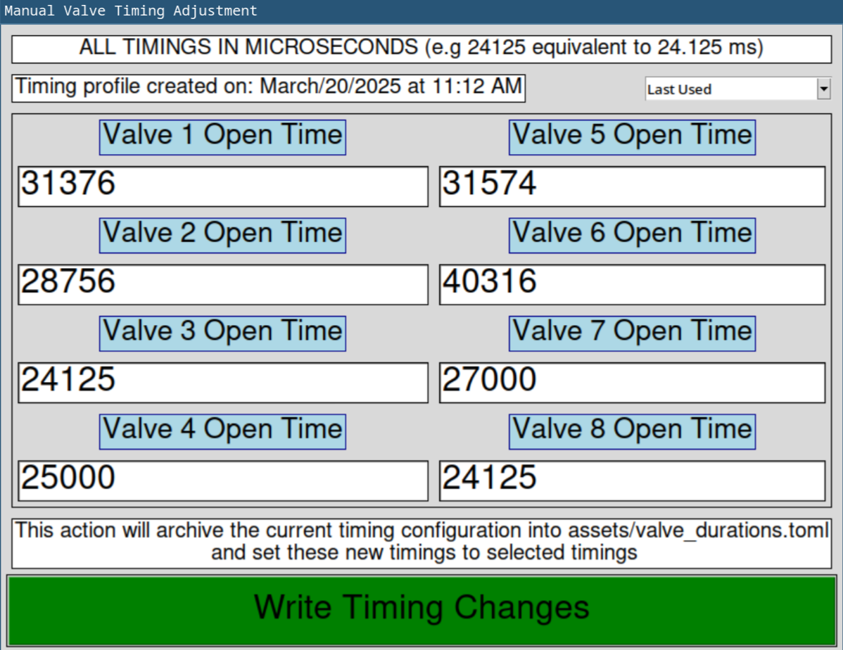
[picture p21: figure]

Figure 13: Users can Override Mistankenly Accepted Automatic Valve Duration Adjustments by Manually Entering New Times in the ‘Manual Valve Timing Adjustment’ window.

27

### 4.2.2 Okay, How do I do it? (Setting Valve Duration Profiles)

Here, users can manually enter different opening times for any of the rig’s currently configured 8 valves and save them as the new selected timings by pressing ‘Write Timing Changes’. However, most people likely do not have the exact timing for a given valve memorized. To aid the user here are different valve timing profiles. To find previously configured or default profiles, click the dropdown menu in the top right of this window as shown in Figure 14.

In this dropdown menu, users have the ability to set durations to one of the following profiles:

- Default: Reset all durations back to the default value of 24125 milliseconds by writing the default profile as the new active profile. This is a good starting point for calibration on fresh valves.
- Last Used: These timings are the most recently used timings and serve as the active timings for the program. At all times, this profile is the one used during experiments. When new timings are written, they are written into this profile.
- Archive 1: Archives are used as ‘back-ups’ of older profiles. Anytime a new profile is written (automatic from a valve-test or manually) the previous ‘profile’ is set to the newest slot in the archive. The newly created profile is then set as the ‘Last Used’ or current profile.

Each time a new archive is added, each archive moves down a slot. For example, if a user writes a new timing profile, the oldest archive profile (‘Archive 3’) is destroyed. Then the contents of archive 2 move to archive 3 (‘Archive 2’ -> ‘Archive 3’). Archive 1 then follows the pattern, moving to slot 2 (‘Archive 1’ -> ‘Archive 2’). This clears the way for the last used profile to be moved to the most recent arhive slot (‘Last Used’ -> ‘Archive 1’). Finally, the newly created profile can be set as the active profile (‘Last used’).

- Archive 2: Archive 2 is the next archival slot, the second oldest of the archive slots.
- Archive 3: Archive 3 is the final archive slot, the oldest of all archives, and is the next profile that will be destroyed upon a new write.

28

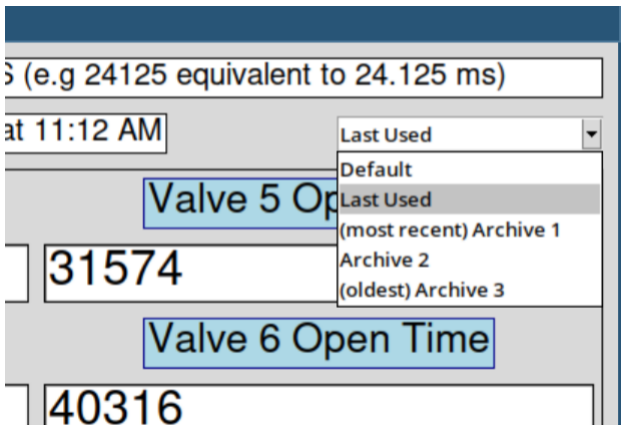
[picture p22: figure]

Figure 14: Users can Restore old Timings via the Timing Profile Dropdown Selection Menu in the ‘Manual Valve Timing Adjustment’ window.

29

### 4.3 Valve Priming

### 4.3.1 Why is this Useful?

The final primary feature of the ‘Valve Testing / Prime Valves’ Window is valve ‘priming’. This is a fancy way of saying "open and close the valves a bunch of times". The reason this is an included feature is that it was found that simply leaving valves open for an extended period of time while downstream tubes were full of only air (in an attempt to fill them with stimulus) did not seem to allow for flow to the tip as desired.

However, it was found that rapidly opening and closing the valves repeatedly did effectively allow for flow all the way down to the tip of the tubes (albeit slowly).

### 4.3.2 Okay, How do I do it? (Priming Valves)

This process is very similar to the process described in Section 4.1. Follow the steps below. This guide assumes that you have the ‘Valve Testing’ window already open on your display as shown in Figure 8

1. Switch to Priming Mode: First, the user should click the orange button labelled ‘Switch to Priming Mode’ as shown in Figure 8. This will change the interface to look like Figure 15.
2. Enter Valve Acutation Number: Next, the user should enter how many times the valve should actuate (open and close) before stopping. The use should enter this value in the entry box under the label titled ‘How Many Times Should the Valve Actuate?’.
3. Select Valves to Prime: Finally, the user should select the buttons corresponding to the valves to be primed. To understand what a valve button looks like when it is selected, refer to Figure 9.
4. Begin Prime Procedure: The application is now ready to begin the procedure. Press the orange ‘Begin Priming’ button to begin.
5. Confirm Prime Settings: The application will generate a pop-up window similar to that shown in Figure 10. The user should review the settings in the pop-up window to confirm these are correct. If they are correct, pressing ‘Yes’ will begin the test procedure.

Note: The procedure can be stopped at any time by pressing the yellow ‘STOP PRIMING’ button. The software does not need to be reset to start a new

30 priming procedure. Once can start and stop as many times as is necessary, changing settings if desired.

After the procedure is complete, check the tubes for the valves just primed. If stimulus has filled the tube to the tip (end nearest spout), then the procedure was successful and the tubes are ready for an experiment. If not, repeat the process.

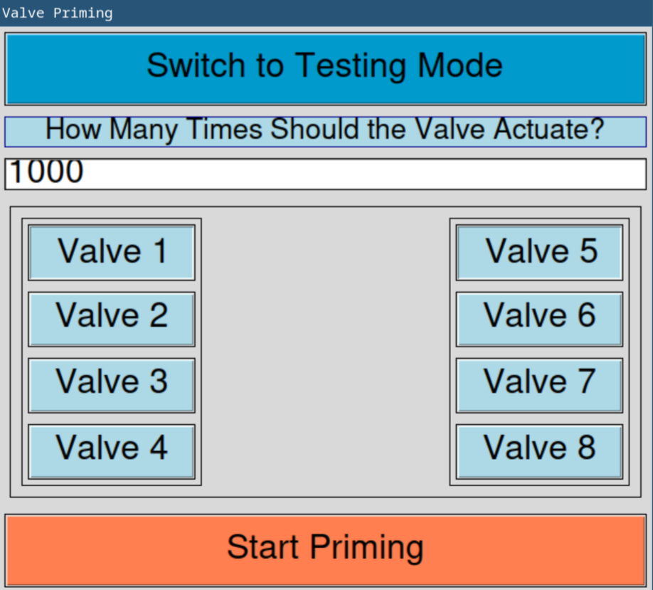
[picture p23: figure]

Figure 15: Users can ‘Prime’ Valve by Clicking ‘Switch to Priming Mode’ in the ‘Valve Test’ Window.

31

## 5 The ‘Valve Control’ Window

### 5.1 What does this Window do?

The ‘Valve Control’ Window is where users can navigate to manually switch on or off valves for arbitrary lengths of time. They may also manually move the rig door up or down in this window. The ‘Valve Control’ window is shown in Figure 16.

### 5.2 Controlling the Valves

All valves begin in the off state and can be switched on by pressing the button corresponding to the valve the user would like to open. Valves will remain open until user selects this button again.

This functionality is particularly useful for pressurizing valves and quickly running cleaning solution through the stimulus delivery tubes.

NOTE: Be aware and mindful that the valves get very hot when left open for long periods of time.

### 5.3 Controlling the Door Motor

The door motor can be moved down by pressing the green ‘Move Motor Down’ button in this window. The door can be left open or closed as long as the user would like and can be moved up and down as many times as necessary.

NOTE: The user should wait until the motor movement is completely finished before pressing the button again to initiate another movement.

Pressing the button before the movement has completed will interfere with the Arduino board’s ability to keep track of the current location of the door and will result in the door moving too far out of range, potentially damaging rig components. Ensure movements have completed before beginning another.

IMPORTANT: The door motor must be in the UP position before starting an experiment. The application assumes this to be the case. If the door is left down, similar symptoms as described in the above note will occur. Ensure the motor is in the UP position before leaving this window and beginning an experiment run.

32

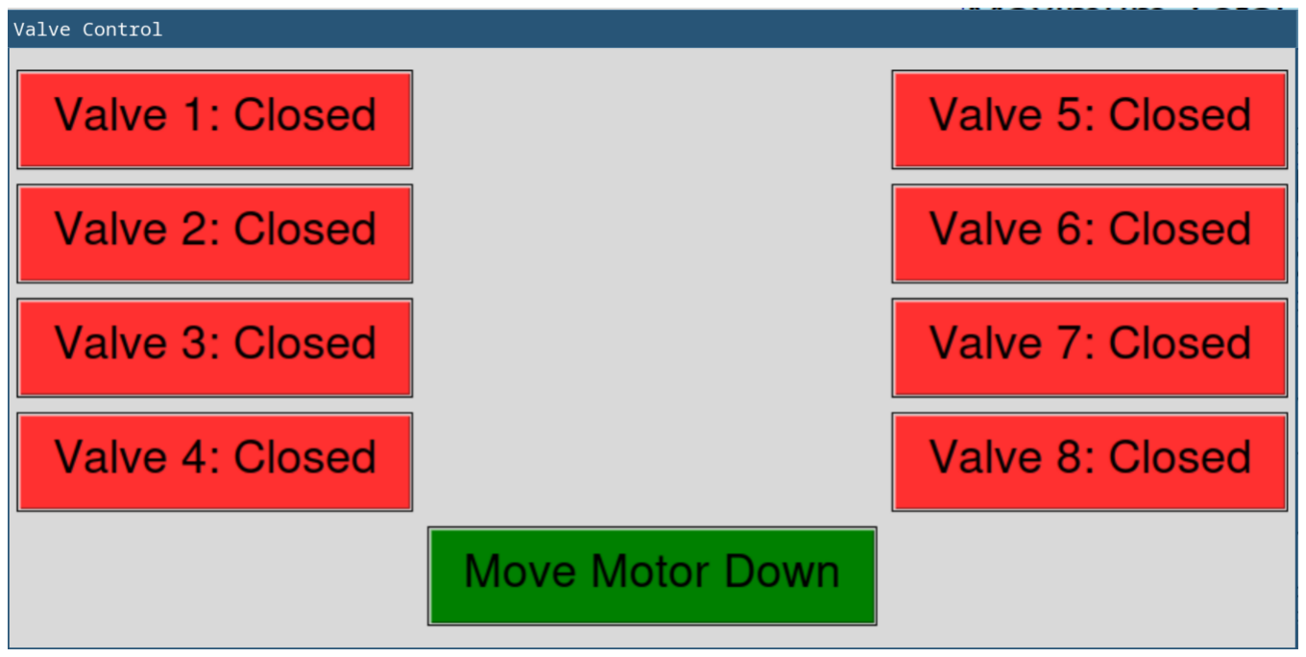
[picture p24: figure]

Figure 16: Users can Manually Control Valves as well as the Door Motor in the ‘Valve Control’ Window.

Figure 17: Valve Buttons Turn Green on User Press Indicating Valve is Now Open. Motor Button Turns Blue upon User Press to Indicate Door is now Down.

33

## 6 The ‘Program Schedule’ Window

### 6.1 What does this Window do?

The ‘Program Schedule’ Window allows the user to view one of the primary ‘dataframe’ components where the software stores experiment data. An example of this window when populated with data from an upcoming experiment is shown in Figure 18.

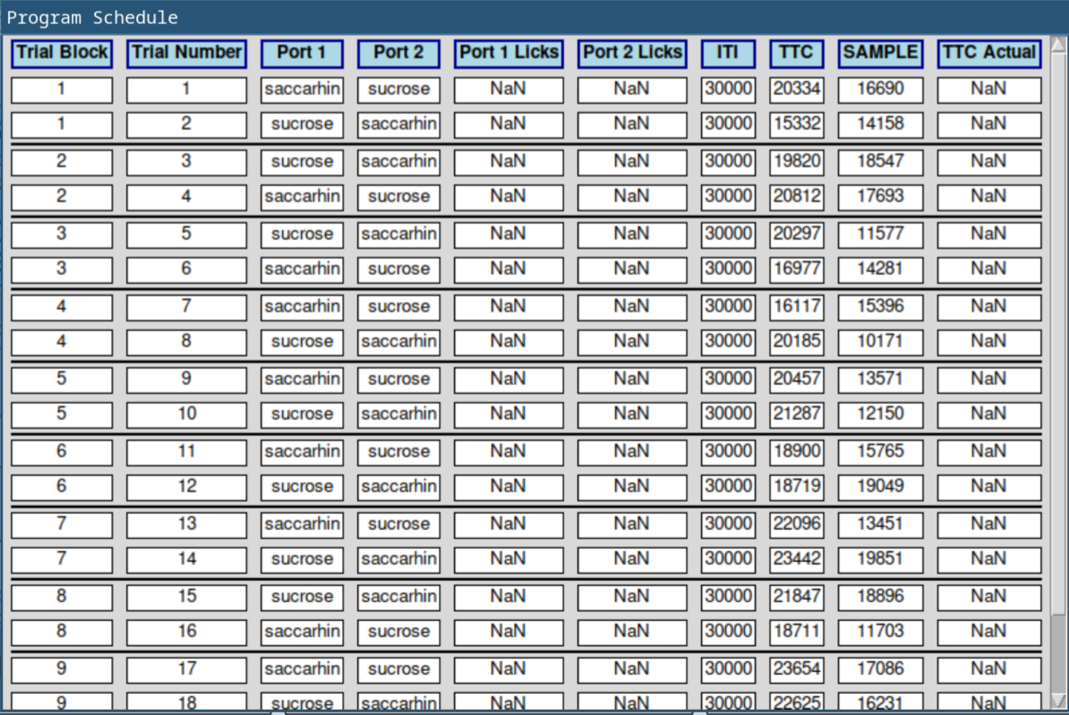
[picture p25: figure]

Figure 18: The Program Schedule Window allows Users to View Basic Current Experiment Data. This Figure Shows the Window Prior to Experiment Beginning, thus the NAN Values for Lick Data.

34

### 6.2 This Window won’t Open due to Error... Why? (Ex-

periment Schedule Error)

The user may see an error when attempting to open this window if they have not yet generated the experiment schedule for the experiment run. The error one may see is shown in Figure 19. The steps to generate the schedule are outlined with references to specific sections in Section 3.1.1.

Figure 19: The Program Schedule window will not Open Until the Program Schedule has been Generated for the Experiment.

### 6.3 What do All these Fields Mean?

This section explains each column, its purpose, and the data/units held within the column’s rows where applicable. Columns are explained from left to right as they appear in the Program Schedule window.

1. Trial Block: A trial block is a group of trials that contain all possible pairings (unique stimuli pairings) of stimuli delivery during an experiment.

For example, for an experiment with two stimuli in use for each port,
(sucrose, saccarhin Port 1 | sucrose, saccarhin Port 2), each stimulus must
be delivered on each port. So there are number of valves / 2 pairings for a trial block. Here there would be 2 trials per block. For the first trial
there may be Port 1: Sucrose | Port 2: Saccarhin. There must also then
be the opposite of this delivery for trial two: Port 1: Saccarhin | Port 2:
Sucrose. This example is shown more clearly in Figure 18.
2. Trial Number: Trial number is simply the trial number of the current trial beginning at 1 and ending at total number of trials.
3. Port 1: Port 1 displays the stimulus to be delivered on Port 1 for the trial in the row.

35

4. Port 2: Port 2 displays the stimulus to be delivered on Port 2 for the trial in the row.
5. Port 1 Licks: Port 1 Licks is updated after a trial occurs and shows the number of times Port 1 was licked for this trial.
6. Port 2 Licks: Port 2 Licks is updated after a trial occurs and shows the number of times Port 2 was licked for this trial.
7. ITI: ITI shows the allocated time for ITI state for a given trial. This time is given in milliseconds.
8. TTC: TTC shows the allocated time for a TTC state for a given trial. This time is given in milliseconds.
9. SAMPLE: SAMPLE shows the allocated time for a Sample state for a given trial. This time is given in milliseconds.
10. TTC Actual: TTC Actual shows the actual time used for a TTC state for a given trial. This is necessary because three rat licks will transition the program into a Sample state early, and will not use all allocated TTC time. This time is given in milliseconds.

36

## 7 The ‘Valve / Stimuli’ Window

### 7.1 What Does this Window Do?

The ‘Valve / Stimuli’ Window is where users should navigate to label the stimuli that will be delivered for a given valve. This is an important step to generating the program schedule as described in Section 3.1.1. The ‘Valve / Stimuli’ window as it will be found on first open is shown in Figure 20.

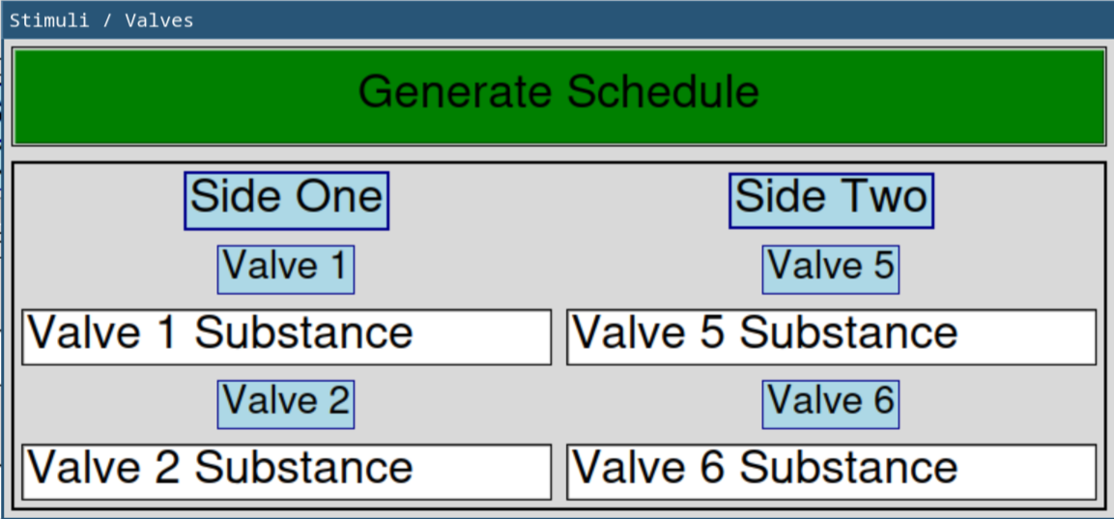
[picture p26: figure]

Figure 20: The ‘Valve / Stimuli’ Window is Initially Filled with Default Values Corresponding to the Labelled Valve Number of a Valve.

### 7.2 How Do I Use this Window? (Generating an Experi-

ment Schedule)

The ‘Valve / Stimuli’ window is where the stimuli schedule is generated for an upcoming experiment. This process will generate not only stimulus lineup for each port per trial for the experiment, but also state base interval times (ITI, TTC, etc) and the random times to be added to these base times. Assuming that interval times and other experiment configuration variables have been set as desired in the main program window (Section 3.4), the remaining step prior to schedule generation is naming the stimuli for each valve.

When assigning stimuli names to valves, the user should start at valve one and continue downwards (enter only in new rows, do not enter in column two). This will simplify the process, as the program will automatically assign names to valves on column two based on names entered in column one. When names have been assigned, users can press the large green ‘Generate Schedule’ button at the top of the ‘Valve / Stimuli’ window.

If this process is successful, the ‘Valve / Stimuli’ window will disappear, and a new ‘Program Schedule’ window will appear displaying the schedule to be followed for the next experiment as shown in Figure 18.

37

## 8 The ‘Event Data’ Window

The ‘Event Data’ Window shows the user more detailed information about events that occur during an experiment run. While the program schedule shows much of the desired information about the experiment to the user, it lacks information like event timestamps, durations, etc. The ‘Event Data’ window fills in these data gaps.

Details about rat licks as well as door motor movement details are contained in this window. Because two different event types are stored here, some columns may not always contain a value. This is discussed in more detail below.

Figure 21: The event data window

### 8.1 Detailed Column Breakdown

Here the contents of each column is discussed in detail. This includes general details as well as units of displayed information where applicable.

1. Trial Number: This column displays the trial that an event occurred in.
2. Licked Port: This column will not always contain a value. It will only be filled if the event being recorded is a rat lick. Motor movement recordings will mark this columns value for this row as ‘nan’.
3. Event Duration: This column is used for both licks and motor movements. It records the length of time the event occurred in from onset to offset.

For licks, this is the time difference between the moment the lick beam is broken until the moment it is restored. For door motor movements, it is the time difference between motor movement instruction until the motor reaches the target position. This time is represented in milliseconds.

4. Valve Duration: Valve duration is only marked for the subset of lick events that occur within the ‘SAMPLE’ state. This is because valves are not opened during ‘TTC’ state. Value stored as nan for licks in ‘TTC’ state or motor movement events. This time is represented in milliseconds.

38

5. Time Stamp: This value is the time the event occurred relative to the program start time (t=0) in seconds.
6. Trial Relative Stamp: This value is the time the event occurred relative to the trial start time. Trial start here is defined as TTC start time, because this is the moment the rat can begin to engage in the trial. This time is represented in seconds.
7. State: State can hold different values depending on the type of event that occurred. Motor movements will state the type of motor movement that occurred (MOTOR [UP, DOWN]). Licks will show the program state at the time of the lick (TTC, SAMPLE).

NOTE: The method by which data in this window is refreshed is pressing the ‘Event Data’ button in the main program window. This button serves as the method to access the window and update with new information that has occurred. The window will NOT automatically refresh. The user must manually trigger updates via this method.

39

## 9 The ‘Rasterized Data’ Window

Pressing the ‘Rasterized Data’ button in the main program window produces two identical raster plots representing the licks per trial per port. This window is useful to ensure that reported licks from the Arduino board seem to match with the accepted understanding of how quickly rats can lick maximally.

In other words, it allows users to ensure that the data being recorded is accurate, and no ‘phantom licks’ are being recorded due to equipment inadequacies or failures.

In this window, the Y-axis represents trial number, while X-axis values represent the time stamp associated with a given lick.

(a) Example of Data Filling the Side (Port) 1 Raster Plot.

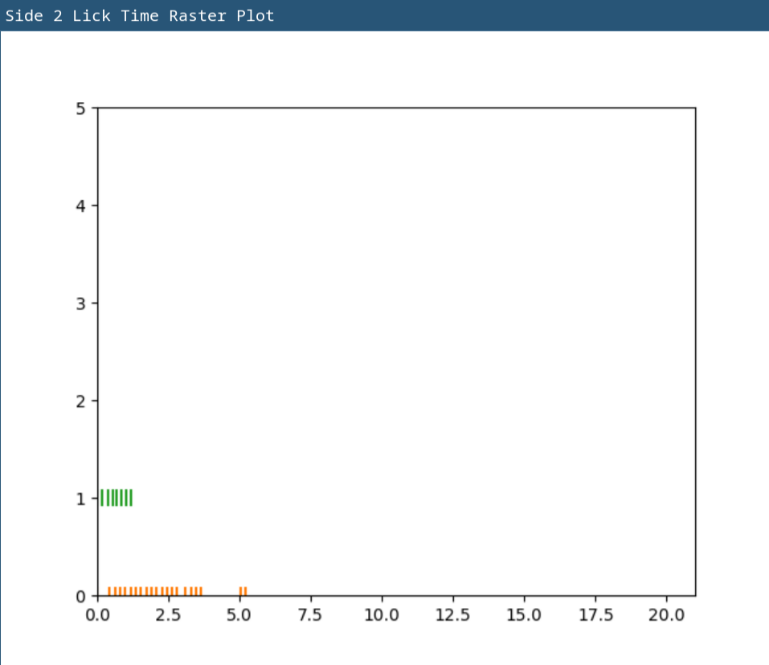
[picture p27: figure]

(b) Example of Data Filling the Side (Port) 2 Raster Plot.

Figure 22: Raster Plots are Seperated by Port to make Analysis more Straightforward.

40

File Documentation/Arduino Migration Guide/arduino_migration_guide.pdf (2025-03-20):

# Photologic Experiment Rig Arduino Migration Guide

Blake Hourigan

March 18, 2025

1

## Contents

1 Why the Migration? | 4
2 The Migration Process | 5
2.1.5 | Remove the ‘Laser Arduino’ board from the Setup . . . . | 9
3 Verifying Functionality | 17
4 Troubleshooting | 21

2

4.4 What to do if the Door Motor does not Move as Expected? . . . | 23
5 In Closing | 24

3

## 1 Why the Migration?

If you are not interested in why but only how to perform the migration, skip to Section 2.

When I began working on this project again after about a year-long hiatus, I was struck by various aspects of the program that were much less effiecient than they should be. I began work to resolve some of these issues individually on the two different Arduino boards. I changed data structures, algorithms, moved to simpler structs rather than classes, etc. and I noticed incredible speed-ups in the tasks being performed on each board. As things became faster and more efficient, I began to wonder if having two distinct Arduino boards was necessary.

The processor on board is incredibly fast and the tasks being performed are so light that it seemed like overkill to have two individual boards performing different tasks. Not to mention the overhead of having two separate boards. Handling communication between two different boards meant that code was required to identify these boards. Often commands needed to be sent to two boards at once rather than combining commands to one board. Furthermore, the Arduino boards needed a mechanism to communicate with each other. The Laser Arduino needed to somehow communicate the fact that a lick has occurred so that the Motor/Valve Arduino could properly respond.

So I became interested in the idea of simplifying this setup. It was just a test at first, but it quickly became clear that this setup would perform similar to, if not better than the previous setup. With the added benefit of being able to easily collect and send lick, valve, and motor timestamp data in one place. This allowed for much easier communication of this data to the controller program.

The most difficult part of the process was creating a algorithm for detecting licks, opening valves, and marking closing times while prohibiting lick detection until this marking occured. The real complication here was that the algorithm could not loop or block the execution of the rest of the code. But once this was finished and various pieces of code were optimized for speed (e.g properly ordering command conditional statements) and testing simulated licks with an onset-to-end duration of as low as 15ms, it was clear that the board could handle these tasks all together. It is able to record and report these data points, handle door motor operation, valve operation, and lick detection all in the same board.

This allows for a simpler setup and slightly lower cost of the rig. But the real benefit here is a greater wealth of data and reduced complexity in communication protocols and physical setup.

For the rest of this article I will detail the steps you must take to migrate your setup from 2 Arduino boards to 1, including hardware and software steps.

4

## 2 The Migration Process

I’ve worked quite hard during this period of development to make distribution of both of the required software packages for the rig as simple and easy as possible. While the Arduino portion of the code is slightly more complex, I’ve tried to detail every step as simply and as verbose as possbile to ensure that anyone can do it. If you follow each step closely, you should be up and running in no time!

If you are someone who is savvy enough, you may use the KiCAD PCB design file, along with the new Arduino source code files to assist you during this process. These are NOT required to complete the migration, but they may be helpful if you get confused or make a misstep along the way.

If you have downloaded the Github repository (https://github.com/blakehourigan/Photologic-Experiment-Rig) locally on your computer, the KiCAD project file you are looking for will be located at ‘/Circuitry/Final PCB.kicad pro’. The Arduino Code is Located at ‘/Code/Arduino Code’. The root Arduino ‘.ino’ file will be located here, with specific function code such as optical sensor pin definition and LED pin definition located under the respective directory inside of the /src directory.

### 2.1 Hardware Migration Steps

First, we will start with the hardware migration steps. Here you are going to eventually remove the Arduino board previously labelled ’Laser Arduino’, leaving only the Arduino board previously labelled or known as the ‘Motor Arduino’. If you don’t know which is which, identification steps are given below.

### 2.1.1 Identify the ‘Laser Arduino’ Board

You are going to first identify which Arduino board is the ‘Laser Arduino’ in your setup. If the board is unhelpfully not labelled, it is the board with wires running to the PCB (circuit board) whose connectors are labelled ‘Laser Power Pins1’ and ‘LED Logic Harness1’. One-by-one, we will migrate every connection here to the board previously known as the ‘Motor Arduino’.

You do not need to remove the actual connectors on the PCB, that will only complicate the process unnecessarily.

5

### 2.1.2 Obtain a Small flat-head Screwdriver

Locate the small flat-head screws that sit atop the Arduino screw terminal boards shown in Figure 1 that secure the non-connector (loose wire) end to the Arduinos. Again, we will remove these wires ONE AT A TIME to simplify this process.

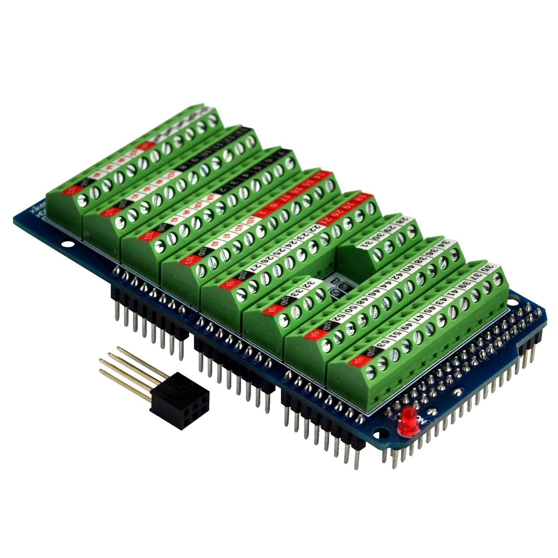
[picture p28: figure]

Figure 1: The Arduino Terminal Screws Sit atop the Arduino Board, and Face Away from You if You Look at the Arduino Head On.

### 2.1.3 Remove Unnecessary Connectors

Now we are going to remove the wires that connect to both Arduino boards that facilitate communication between them.

1. Digital Pin 8 - We will begin with digital pin number 8 which functioned as the lick side indicator previously. This pin should be the same on both Arduino boards.
(a) Locate Digital Pin 8 - Locate the wire attached to digital pin 8 on the ‘Laser Arduino’ board. It is the terminal with the big number 8 on it and the square will be black.
(b) Unscrew the Terminal - Unscrew the terminal with your screwdriver and remove the wire. Follow the wire to the connection on the ‘Motor Arduino’ and repeat the process.

6

(c) Tighten the Terminal Screw - Tighten the terminal screw back down on both Arduino screw terminal boards.
2. Digital Pin 7 - Next, we will remove digital pin 7 which functioned previously as the lick detected signal. This pin is slightly different because it is not the same on both boards. It is pin 7 on the ‘Laser Arduino’, and is pin number 2 on the ‘Motor Arduino’.
(a) Locate Digital Pin 7 - Locate the wire attached to digital pin 7 on the ‘Laser Arduino’ board. It is the terminal with the big number 7 on it and is shaded black.
(b) Unscrew the Terminal - Unscrew the terminal with your screwdriver and remove the wire. Follow the wire to the connection on the ‘Motor Arduino’ and repeat the process.
(c) Tighten the Terminal Screw - Tighten the terminal screw back down on both Arduino screw terminal boards.

### 2.1.4 Migrating the Remaining PCB Connectors

Now that we have removed the inter-Arduino communication connections, we just need to migrate the ‘Laser Arduino’ PCB connector wires to the ‘Motor Arduino’. As dicussed above, these include the below connections from the PCB. As before, we will move wires one-by-one starting at the top of the list and moving downwards.

1. Laser Power Pins1
This connector is the easier of the two to migrate. It is just two connectors, 5V and GND.
(a) Locate the 5V Wire - This wire should have red tape wrapped around it and run to a 5V terminal on the ‘Laser Arduino’ board.
(b) Remove the Wire from Screw Terminal - Unscrew the terminal screw that this wire runs to on the ‘Laser Arduino’, and remove the wire from the terminal.
(c) Locate a Free (unused) 5V Terminal on ‘Motor Arduino’ -Find a free 5V slot on the ‘Motor Arduino’ and unscrew the terminal screw.
(d) Secure the Wire into the Terminal - This step is likely to be one of the more challenging parts of the migration. The wire may not reach because it was not originally designed to stretch that far. You may have to play with the location of the ‘Motor Arduino’ board or solder extra wire to get it to reach.
Once you have situated the boards such that all wires reach their terminals, insert the wire into the open terminal and fasten the wire

7

by tightening the screw until the wire is secure and will not pull from its terminal.
NOTE: You should pinch the wire with your finger and twist the end around until all of the wire is bundled together cleanly to avoid the wire touching another terminal or not fitting into the terminal well. You should do this every time you insert a wire from this point forward.
(e) Locate and Unscrew the Terminal for the GND Wire - Now, take the other wire from the same connector (the one not wrapped in red tape) and remove it from its screw terminal on the ‘Laser Arduino’.
(f) Locate a Free GND Terminal on the ‘Motor Arduino’ - Locate a open GND Terminal on the ‘Motor Arduino’, unscrew the terminal, insert the wire, and tighten the screw until the wire is secure and will not pull from its terminal.
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

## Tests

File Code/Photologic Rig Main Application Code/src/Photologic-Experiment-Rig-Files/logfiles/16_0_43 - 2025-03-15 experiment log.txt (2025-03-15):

2025-03-15 16:00:43,982 - INFO - Licks dataframe initialized.
2025-03-15 16:00:44,035 - INFO - Arduino connected on port COM3
2025-03-15 16:00:44,035 - INFO - Connected to Arduino boards successfully.
2025-03-15 16:00:44,305 - INFO - Timer 'Time Elapsed:' created.
2025-03-15 16:00:44,305 - INFO - Timer 'Maximum Total Time:' created.
2025-03-15 16:00:44,305 - INFO - Timer 'State Time:' created.
2025-03-15 16:00:44,305 - INFO - Timers displayed.
2025-03-15 16:00:44,311 - INFO - Labeled entry 'ITI Time' created.
2025-03-15 16:00:44,311 - INFO - Labeled entry 'TTC Time' created.
2025-03-15 16:00:44,311 - INFO - Labeled entry 'Sample Time' created.
2025-03-15 16:00:44,311 - INFO - Labeled entry '# Trial Blocks' created.
2025-03-15 16:00:44,313 - INFO - Labeled entry '+/- ITI' created.
2025-03-15 16:00:44,313 - INFO - Labeled entry '+/- TTC' created.
2025-03-15 16:00:44,313 - INFO - Labeled entry '+/- Sample' created.
2025-03-15 16:00:44,313 - INFO - Labeled entry '# Stimuli' created.
2025-03-15 16:00:44,313 - INFO - Entry widgets displayed.
2025-03-15 16:00:44,313 - INFO - Button 'Start' created.
2025-03-15 16:00:44,313 - INFO - Button 'Reset' created.
2025-03-15 16:00:44,313 - INFO - Main control buttons displayed.
2025-03-15 16:00:44,315 - INFO - Button 'Valve Testing / Prime Valves' created.
2025-03-15 16:00:44,315 - INFO - Button 'Valve Control' created.
2025-03-15 16:00:44,315 - INFO - Button 'Program Schedule' created.
2025-03-15 16:00:44,315 - INFO - Button 'Valve / Stimuli' created.
2025-03-15 16:00:44,315 - INFO - Button 'Event Data' created.
2025-03-15 16:00:44,315 - INFO - Button 'Rasterized Data' created.
2025-03-15 16:00:44,315 - INFO - Button 'Save Data' created.
2025-03-15 16:00:44,315 - INFO - Lower control buttons displayed.
2025-03-15 16:00:44,319 - INFO - Status widget displayed.
2025-03-15 16:00:44,319 - INFO - GUI setup completed.
2025-03-15 16:00:44,320 - INFO - Labeled entry 'Valve 1' created.
2025-03-15 16:00:44,320 - INFO - Labeled entry 'Valve 2' created.
2025-03-15 16:00:44,321 - INFO - Labeled entry 'Valve 5' created.
2025-03-15 16:00:44,321 - INFO - Labeled entry 'Valve 6' created.
2025-03-15 16:00:44,321 - INFO - Stimuli frame populated.
2025-03-15 16:00:44,321 - INFO - Button 'Generate Schedule' created.
2025-03-15 16:00:44,321 - INFO - Filled contents of experiment control window.
2025-03-15 16:00:44,321 - INFO - Experiment Control Window created, but hidden for now.
2025-03-15 16:00:44,535 - INFO - Button 'Switch to Priming Mode' created.
2025-03-15 16:00:44,535 - INFO - Labeled entry 'Desired Dispensed Volume in Microliters (ul)' created.
2025-03-15 16:00:44,535 - INFO - Labeled entry 'How Many Times Should the Valve Actuate?' created.
2025-03-15 16:00:44,535 - ERROR - Initialization error: name 'Path' is not defined

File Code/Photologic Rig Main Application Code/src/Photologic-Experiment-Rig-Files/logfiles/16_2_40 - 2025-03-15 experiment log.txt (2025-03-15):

2025-03-15 16:02:40,035 - INFO - Licks dataframe initialized.
2025-03-15 16:02:40,068 - INFO - Arduino connected on port COM3
2025-03-15 16:02:40,068 - INFO - Connected to Arduino boards successfully.
2025-03-15 16:02:40,118 - INFO - Timer 'Time Elapsed:' created.
2025-03-15 16:02:40,118 - INFO - Timer 'Maximum Total Time:' created.
2025-03-15 16:02:40,118 - INFO - Timer 'State Time:' created.
2025-03-15 16:02:40,118 - INFO - Timers displayed.
2025-03-15 16:02:40,118 - INFO - Labeled entry 'ITI Time' created.
2025-03-15 16:02:40,118 - INFO - Labeled entry 'TTC Time' created.
2025-03-15 16:02:40,118 - INFO - Labeled entry 'Sample Time' created.
2025-03-15 16:02:40,118 - INFO - Labeled entry '# Trial Blocks' created.
2025-03-15 16:02:40,118 - INFO - Labeled entry '+/- ITI' created.
2025-03-15 16:02:40,118 - INFO - Labeled entry '+/- TTC' created.
2025-03-15 16:02:40,118 - INFO - Labeled entry '+/- Sample' created.
2025-03-15 16:02:40,118 - INFO - Labeled entry '# Stimuli' created.
2025-03-15 16:02:40,118 - INFO - Entry widgets displayed.
2025-03-15 16:02:40,118 - INFO - Button 'Start' created.
2025-03-15 16:02:40,118 - INFO - Button 'Reset' created.
2025-03-15 16:02:40,118 - INFO - Main control buttons displayed.
2025-03-15 16:02:40,118 - INFO - Button 'Valve Testing / Prime Valves' created.
2025-03-15 16:02:40,134 - INFO - Button 'Valve Control' created.
2025-03-15 16:02:40,134 - INFO - Button 'Program Schedule' created.
2025-03-15 16:02:40,134 - INFO - Button 'Valve / Stimuli' created.
2025-03-15 16:02:40,134 - INFO - Button 'Event Data' created.
2025-03-15 16:02:40,134 - INFO - Button 'Rasterized Data' created.
2025-03-15 16:02:40,135 - INFO - Button 'Save Data' created.
2025-03-15 16:02:40,135 - INFO - Lower control buttons displayed.
2025-03-15 16:02:40,136 - INFO - Status widget displayed.
2025-03-15 16:02:40,136 - INFO - GUI setup completed.
2025-03-15 16:02:40,137 - INFO - Labeled entry 'Valve 1' created.
2025-03-15 16:02:40,138 - INFO - Labeled entry 'Valve 2' created.
2025-03-15 16:02:40,138 - INFO - Labeled entry 'Valve 5' created.
2025-03-15 16:02:40,138 - INFO - Labeled entry 'Valve 6' created.
2025-03-15 16:02:40,138 - INFO - Stimuli frame populated.
2025-03-15 16:02:40,138 - INFO - Button 'Generate Schedule' created.
2025-03-15 16:02:40,139 - INFO - Filled contents of experiment control window.
2025-03-15 16:02:40,139 - INFO - Experiment Control Window created, but hidden for now.
2025-03-15 16:02:40,285 - INFO - Button 'Switch to Priming Mode' created.
2025-03-15 16:02:40,285 - INFO - Labeled entry 'Desired Dispensed Volume in Microliters (ul)' created.
2025-03-15 16:02:40,285 - INFO - Labeled entry 'How Many Times Should the Valve Actuate?' created.
2025-03-15 16:02:40,285 - ERROR - Initialization error: name 'Path' is not defined

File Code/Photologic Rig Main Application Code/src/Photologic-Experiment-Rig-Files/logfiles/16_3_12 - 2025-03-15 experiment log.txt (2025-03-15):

2025-03-15 16:03:12,598 - INFO - Licks dataframe initialized.
2025-03-15 16:03:12,652 - INFO - Arduino connected on port COM3
2025-03-15 16:03:12,652 - INFO - Connected to Arduino boards successfully.
2025-03-15 16:03:12,701 - INFO - Timer 'Time Elapsed:' created.
2025-03-15 16:03:12,701 - INFO - Timer 'Maximum Total Time:' created.
2025-03-15 16:03:12,702 - INFO - Timer 'State Time:' created.
2025-03-15 16:03:12,702 - INFO - Timers displayed.
2025-03-15 16:03:12,703 - INFO - Labeled entry 'ITI Time' created.
2025-03-15 16:03:12,703 - INFO - Labeled entry 'TTC Time' created.
2025-03-15 16:03:12,706 - INFO - Labeled entry 'Sample Time' created.
2025-03-15 16:03:12,706 - INFO - Labeled entry '# Trial Blocks' created.
2025-03-15 16:03:12,706 - INFO - Labeled entry '+/- ITI' created.
2025-03-15 16:03:12,706 - INFO - Labeled entry '+/- TTC' created.
2025-03-15 16:03:12,706 - INFO - Labeled entry '+/- Sample' created.
2025-03-15 16:03:12,706 - INFO - Labeled entry '# Stimuli' created.
2025-03-15 16:03:12,706 - INFO - Entry widgets displayed.
2025-03-15 16:03:12,706 - INFO - Button 'Start' created.
2025-03-15 16:03:12,706 - INFO - Button 'Reset' created.
2025-03-15 16:03:12,706 - INFO - Main control buttons displayed.
2025-03-15 16:03:12,706 - INFO - Button 'Valve Testing / Prime Valves' created.
2025-03-15 16:03:12,706 - INFO - Button 'Valve Control' created.
2025-03-15 16:03:12,706 - INFO - Button 'Program Schedule' created.
2025-03-15 16:03:12,706 - INFO - Button 'Valve / Stimuli' created.
2025-03-15 16:03:12,706 - INFO - Button 'Event Data' created.
2025-03-15 16:03:12,706 - INFO - Button 'Rasterized Data' created.
2025-03-15 16:03:12,706 - INFO - Button 'Save Data' created.
2025-03-15 16:03:12,706 - INFO - Lower control buttons displayed.
2025-03-15 16:03:12,706 - INFO - Status widget displayed.
2025-03-15 16:03:12,706 - INFO - GUI setup completed.
2025-03-15 16:03:12,706 - INFO - Labeled entry 'Valve 1' created.
2025-03-15 16:03:12,706 - INFO - Labeled entry 'Valve 2' created.
2025-03-15 16:03:12,706 - INFO - Labeled entry 'Valve 5' created.
2025-03-15 16:03:12,706 - INFO - Labeled entry 'Valve 6' created.
2025-03-15 16:03:12,706 - INFO - Stimuli frame populated.
2025-03-15 16:03:12,706 - INFO - Button 'Generate Schedule' created.
2025-03-15 16:03:12,706 - INFO - Filled contents of experiment control window.
2025-03-15 16:03:12,706 - INFO - Experiment Control Window created, but hidden for now.
2025-03-15 16:03:12,868 - INFO - Button 'Switch to Priming Mode' created.
2025-03-15 16:03:12,868 - INFO - Labeled entry 'Desired Dispensed Volume in Microliters (ul)' created.
2025-03-15 16:03:12,868 - INFO - Labeled entry 'How Many Times Should the Valve Actuate?' created.
2025-03-15 16:03:12,885 - INFO - Button 'Valve 1' created.
2025-03-15 16:03:12,885 - INFO - Button 'Valve 5' created.
2025-03-15 16:03:12,885 - INFO - Button 'Valve 2' created.
2025-03-15 16:03:12,885 - INFO - Button 'Valve 6' created.
2025-03-15 16:03:12,885 - INFO - Button 'Valve 3' created.
2025-03-15 16:03:12,885 - INFO - Button 'Valve 7' created.
2025-03-15 16:03:12,885 - INFO - Button 'Valve 4' created.
2025-03-15 16:03:12,885 - INFO - Button 'Valve 8' created.
2025-03-15 16:03:12,885 - INFO - Button 'Start Testing' created.
2025-03-15 16:03:12,918 - INFO - Experiment control window centered.
2025-03-15 16:03:12,935 - INFO - Labeled entry 'Valve 1 Open Time' created.
2025-03-15 16:03:12,935 - INFO - Labeled entry 'Valve 5 Open Time' created.
2025-03-15 16:03:12,935 - INFO - Labeled entry 'Valve 2 Open Time' created.
2025-03-15 16:03:12,935 - INFO - Labeled entry 'Valve 6 Open Time' created.
2025-03-15 16:03:12,935 - INFO - Labeled entry 'Valve 3 Open Time' created.
2025-03-15 16:03:12,935 - INFO - Labeled entry 'Valve 7 Open Time' created.
2025-03-15 16:03:12,935 - INFO - Labeled entry 'Valve 4 Open Time' created.
2025-03-15 16:03:12,935 - INFO - Labeled entry 'Valve 8 Open Time' created.
2025-03-15 16:03:12,935 - INFO - Button 'Write Timing Changes' created.
2025-03-15 16:03:12,935 - INFO - Valve Test Window initialized.
2025-03-15 16:03:12,935 - INFO - Button 'Valve 1: Closed' created.
2025-03-15 16:03:12,935 - INFO - Button 'Valve 5: Closed' created.
2025-03-15 16:03:12,935 - INFO - Button 'Valve 2: Closed' created.
2025-03-15 16:03:12,935 - INFO - Button 'Valve 6: Closed' created.
2025-03-15 16:03:12,935 - INFO - Button 'Valve 3: Closed' created.
2025-03-15 16:03:12,935 - INFO - Button 'Valve 7: Closed' created.
2025-03-15 16:03:12,935 - INFO - Button 'Valve 4: Closed' created.
2025-03-15 16:03:12,935 - INFO - Button 'Valve 8: Closed' created.
2025-03-15 16:03:12,935 - INFO - Button 'Move Motor Down' created.
2025-03-15 16:03:12,935 - INFO - MainGUI initialized.
2025-03-15 16:03:12,935 - INFO - GUI started successfully.
2025-03-15 16:03:22,324 - INFO - Application closed.

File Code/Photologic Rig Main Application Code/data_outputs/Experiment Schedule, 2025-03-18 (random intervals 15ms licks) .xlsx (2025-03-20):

Trial Block | Trial Number | Port 1 | Port 2 | Port 1 Licks | Port 2 Licks | ITI | TTC | SAMPLE | TTC Actual
1 | 1 | sour | sweet | 0 | 420 | 30000 | 20987 | 18935 | 322.613
1 | 2 | sucrose | saccarhin | 291 | 0 | 30000 | 17440 | 13222 | 126.954
1 | 3 | sweet | sour | 0 | 353 | 30000 | 20036 | 15980 | 286.165
1 | 4 | saccarhin | sucrose | 375 | 0 | 30000 | 21113 | 16974 | 306.503
2 | 5 | sucrose | saccarhin | 0 | 392 | 30000 | 21933 | 17717 | 323.299
2 | 6 | sour | sweet | 347 | 0 | 30000 | 21234 | 15663 | 339.212
2 | 7 | saccarhin | sucrose | 125 | 283 | 30000 | 18633 | 18564 | 376.582
2 | 8 | sweet | sour | 148 | 193 | 30000 | 18143 | 15558 | 250.551
3 | 9 | sweet | sour | 211 | 80 | 30000 | 15018 | 13276 | 233.502
3 | 10 | sucrose | saccarhin | 62 | 234 | 30000 | 23021 | 13556 | 239.501
3 | 11 | sour | sweet | 235 | 39 | 30000 | 22449 | 12438 | 218.525
3 | 12 | saccarhin | sucrose | 38 | 259 | 30000 | 24935 | 13586 | 326.293
4 | 13 | sweet | sour | 422 | 15 | 30000 | 21219 | 19899 | 187.216
4 | 14 | sour | sweet | 0 | 425 | 30000 | 17835 | 19348 | 190.977
4 | 15 | sucrose | saccarhin | 280 | 0 | 30000 | 18358 | 12851 | 242.648
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

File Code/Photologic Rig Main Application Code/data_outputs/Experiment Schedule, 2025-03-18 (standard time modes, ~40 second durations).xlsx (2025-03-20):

Trial Block | Trial Number | Port 1 | Port 2 | Port 1 Licks | Port 2 Licks | ITI | TTC | SAMPLE | TTC Actual
1 | 1 | Sweet | Sour | 158 | 6 | 30000 | 21300 | 12378 | 379.944
1 | 2 | Saccarhin | Sucrose | 221 | 0 | 30000 | 20314 | 16830 | 327.094
1 | 3 | Sucrose | Saccarhin | 0 | 168 | 30000 | 15949 | 11836 | 405.591
1 | 4 | Sour | Sweet | 172 | 92 | 30000 | 17015 | 19412 | 375.167
2 | 5 | Sucrose | Saccarhin | 188 | 0 | 30000 | 20105 | 14219 | 350.381
2 | 6 | Sour | Sweet | 0 | 244 | 30000 | 19925 | 17216 | 253.042
2 | 7 | Saccarhin | Sucrose | 149 | 41 | 30000 | 20515 | 14092 | 291.221
2 | 8 | Sweet | Sour | 221 | 0 | 30000 | 15495 | 16807 | 382.375
3 | 9 | Sucrose | Saccarhin | 0 | 165 | 30000 | 15770 | 11601 | 431.538
3 | 10 | Sweet | Sour | 120 | 105 | 30000 | 16145 | 16480 | 360.991
3 | 11 | Saccarhin | Sucrose | 197 | 0 | 30000 | 20200 | 15068 | 263.878
3 | 12 | Sour | Sweet | 0 | 183 | 30000 | 23321 | 13022 | 413.17
4 | 13 | Sweet | Sour | 37 | 140 | 30000 | 24108 | 12797 | 449.393
4 | 14 | Sour | Sweet | 184 | 0 | 30000 | 18713 | 14045 | 421.386
4 | 15 | Sucrose | Saccarhin | 0 | 216 | 30000 | 20458 | 15326 | 427.283
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

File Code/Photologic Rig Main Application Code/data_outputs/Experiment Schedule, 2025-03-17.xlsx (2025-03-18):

Trial Block | Trial Number | Port 1 | Port 2 | Port 1 Licks | Port 2 Licks | ITI | TTC | SAMPLE | TTC Actual
1 | 1 | sour | sweet | 65 | 41 | 5000 | 5000 | 5000 | 104.0654182
1 | 2 | sucrose | saccarhin | 0 | 106 | 5000 | 5000 | 5000 | 162.2185707
1 | 3 | saccarhin | sucrose | 0 | 106 | 5000 | 5000 | 5000 | 169.832468
1 | 4 | sweet | sour | 0 | 106 | 5000 | 5000 | 5000 | 174.0574837
2 | 5 | sweet | sour | 107 | 0 | 5000 | 5000 | 5000 | 171.328783
2 | 6 | saccarhin | sucrose | 106 | 0 | 5000 | 5000 | 5000 | 177.3412228
2 | 7 | sour | sweet | 106 | 0 | 5000 | 5000 | 5000 | 174.0810871
2 | 8 | sucrose | saccarhin | 106 | 0 | 5000 | 5000 | 5000 | 174.0903854
3 | 9 | sour | sweet | 0 | 107 | 5000 | 5000 | 5000 | 175.2786636
3 | 10 | sweet | sour | 0 | 106 | 5000 | 5000 | 5000 | 176.1007309
3 | 11 | saccarhin | sucrose | 0 | 106 | 5000 | 5000 | 5000 | 177.9711246
3 | 12 | sucrose | saccarhin | 101 | 5 | 5000 | 5000 | 5000 | 174.6385098
4 | 13 | sucrose | saccarhin | 106 | 0 | 5000 | 5000 | 5000 | 179.9426079
4 | 14 | sour | sweet | 106 | 0 | 5000 | 5000 | 5000 | 174.2255688
4 | 15 | sweet | sour | 106 | 0 | 5000 | 5000 | 5000 | 176.1066914
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

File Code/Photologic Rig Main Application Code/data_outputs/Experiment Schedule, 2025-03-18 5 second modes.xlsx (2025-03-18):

Trial Block | Trial Number | Port 1 | Port 2 | Port 1 Licks | Port 2 Licks | ITI | TTC | SAMPLE | TTC Actual
1 | 1 | saccarhin | sucrose | 106 | 0 | 5000 | 5000 | 5000 | 152.279
1 | 2 | sucrose | saccarhin | 106 | 0 | 5000 | 5000 | 5000 | 171.556
1 | 3 | sour | sweet | 106 | 0 | 5000 | 5000 | 5000 | 176.822
1 | 4 | sweet | sour | 0 | 106 | 5000 | 5000 | 5000 | 175.729
2 | 5 | sour | sweet | 0 | 106 | 5000 | 5000 | 5000 | 175.909
2 | 6 | sweet | sour | 0 | 106 | 5000 | 5000 | 5000 | 176.606
2 | 7 | sucrose | saccarhin | 106 | 0 | 5000 | 5000 | 5000 | 424.092
2 | 8 | saccarhin | sucrose | 106 | 0 | 5000 | 5000 | 5000 | 174.65
3 | 9 | sweet | sour | 107 | 0 | 5000 | 5000 | 5000 | 174.261
3 | 10 | sour | sweet | 106 | 0 | 5000 | 5000 | 5000 | 176.92
3 | 11 | saccarhin | sucrose | 0 | 106 | 5000 | 5000 | 5000 | 176.887
3 | 12 | sucrose | saccarhin | 0 | 107 | 5000 | 5000 | 5000 | 174.914
4 | 13 | sucrose | saccarhin | 0 | 106 | 5000 | 5000 | 5000 | 177.808
4 | 14 | saccarhin | sucrose | 62 | 44 | 5000 | 5000 | 5000 | 176.939
4 | 15 | sour | sweet | 107 | 0 | 5000 | 5000 | 5000 | 174.759
4 | 16 | sweet | sour | 106 | 0 | 5000 | 5000 | 5000 | 174.886
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

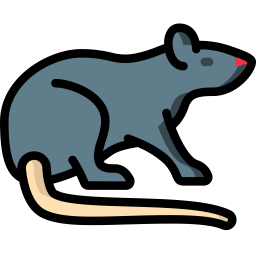
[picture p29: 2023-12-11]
Code/Photologic Rig Main Application Code/src/Photologic-Experiment-Rig-Files/assets/rat.png

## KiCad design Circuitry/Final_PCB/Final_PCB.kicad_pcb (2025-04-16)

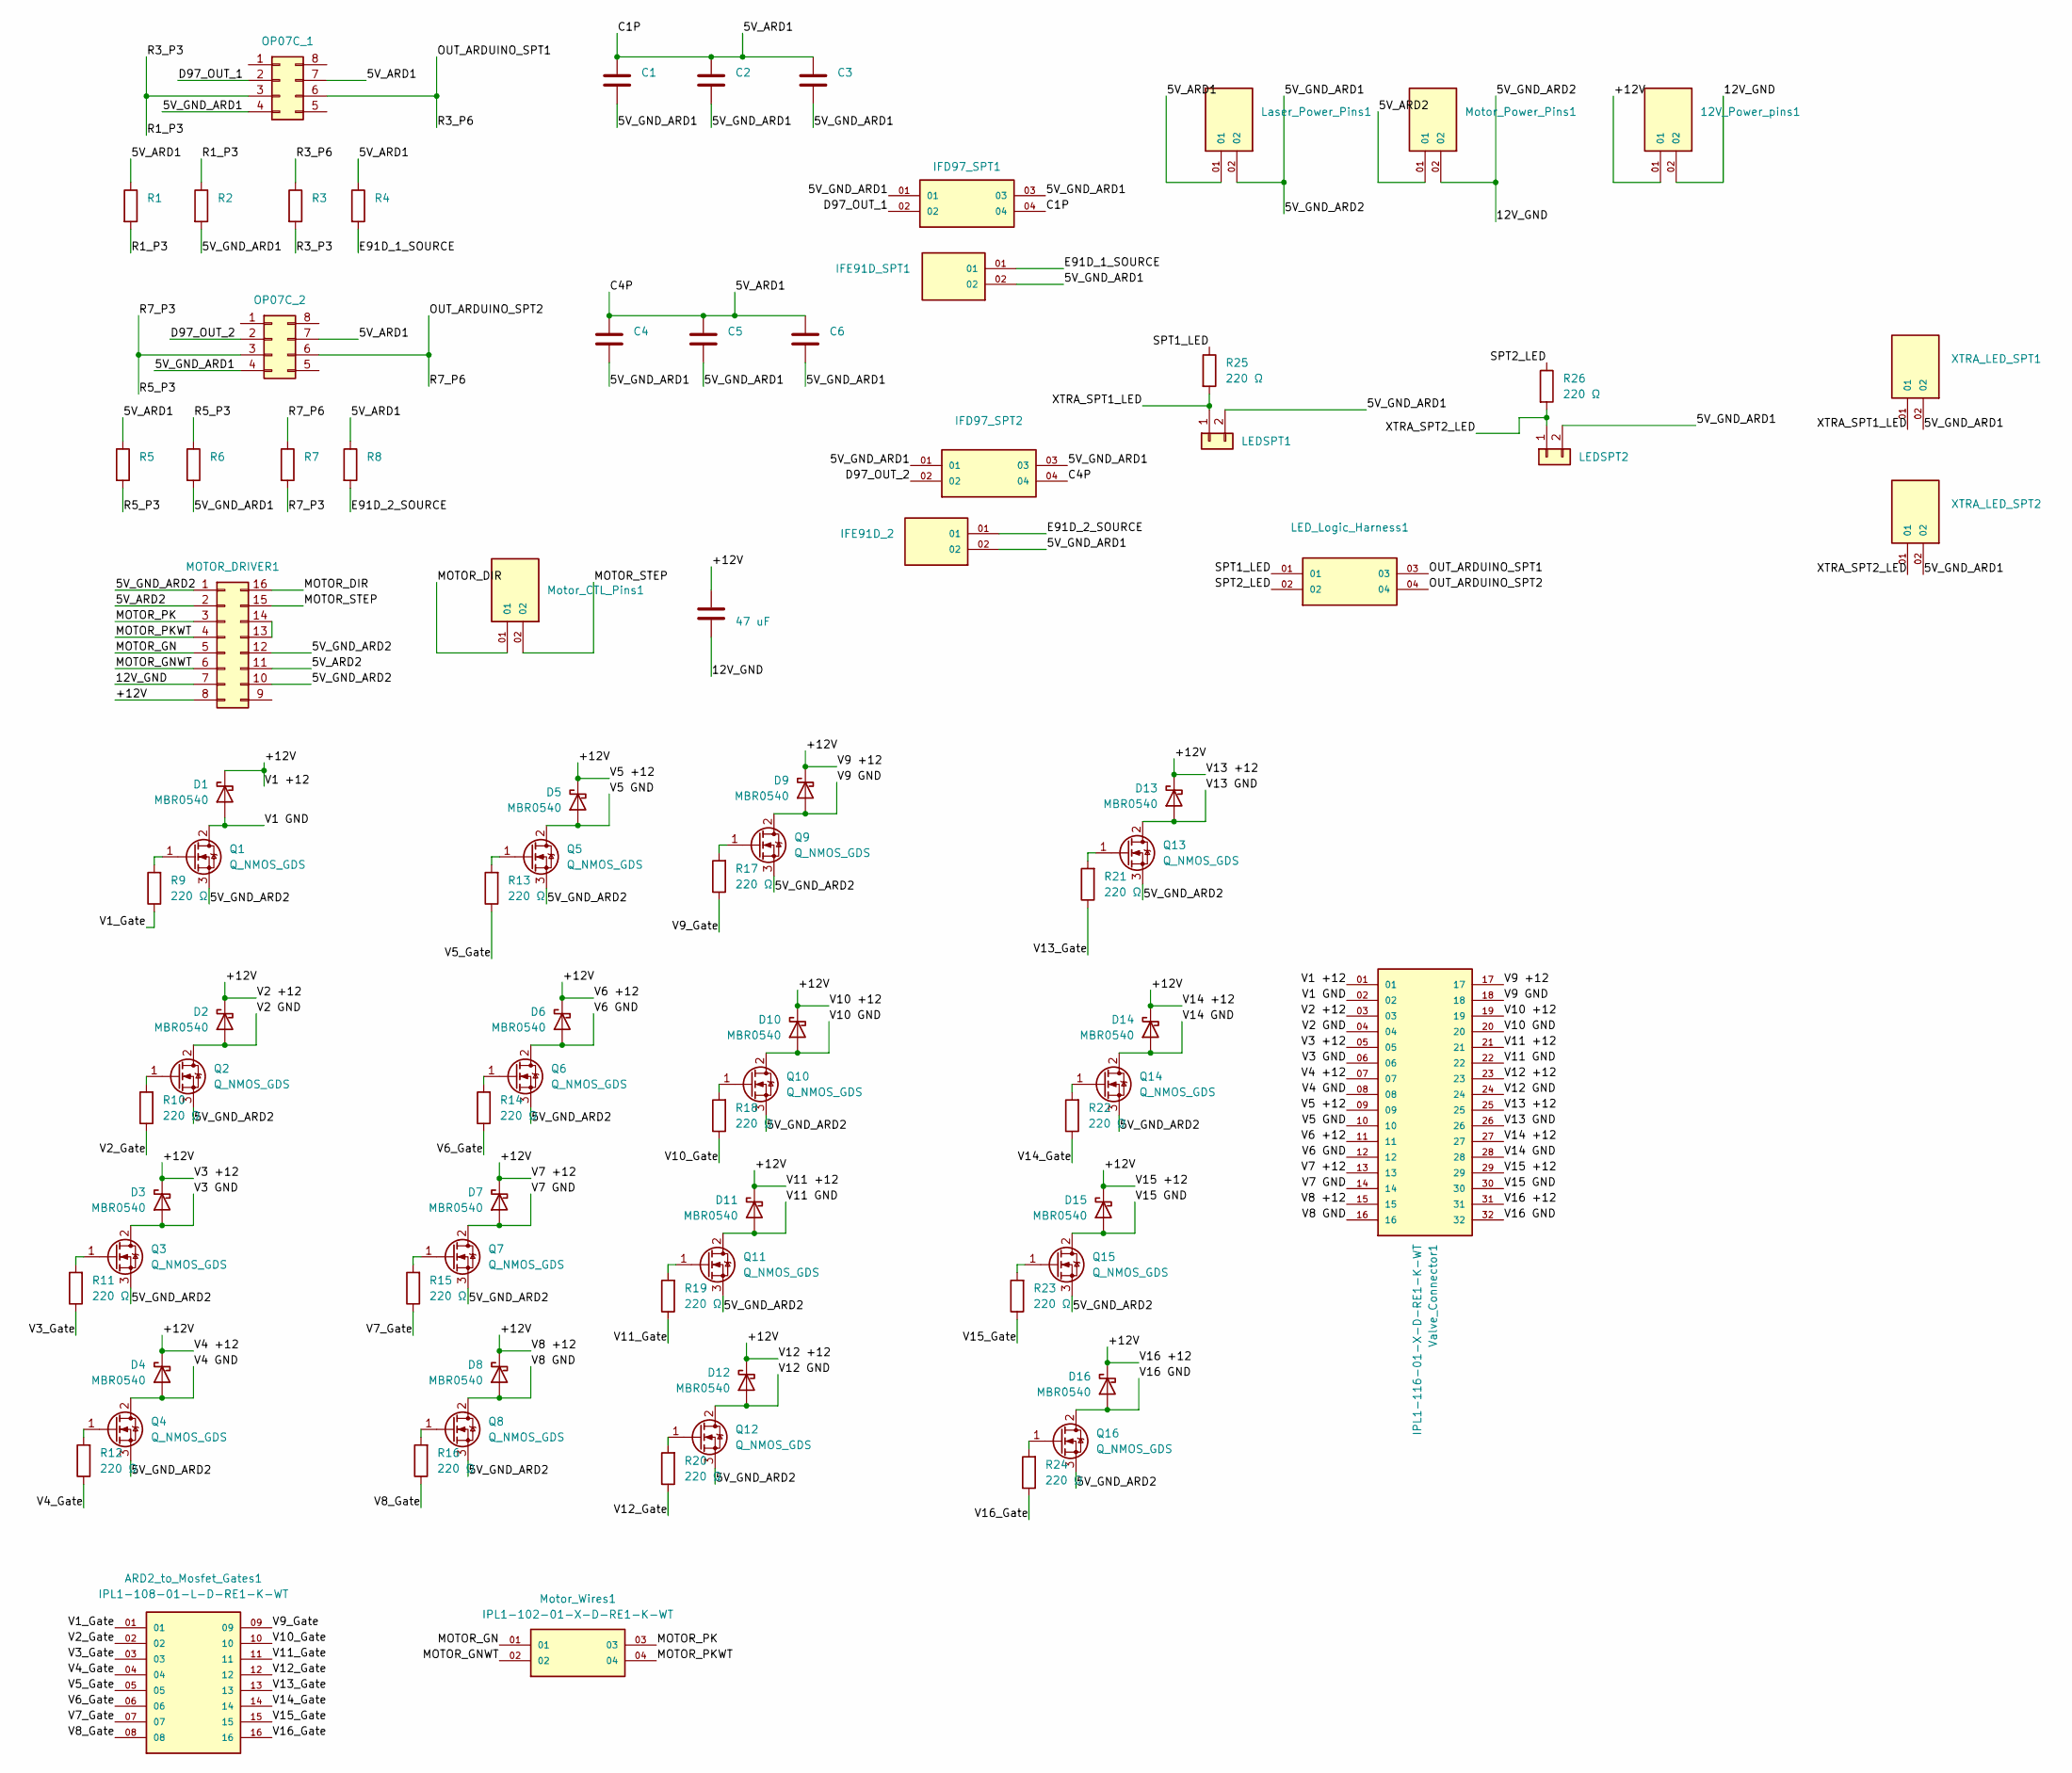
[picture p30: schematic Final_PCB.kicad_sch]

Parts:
12V_Power_pins1: IPL1-102-01-L-S-RE1-K-WT; SAMTEC_IPL1-102-01-L-S-RE1-K-WT
ARD2_to_Mosfet_Gates1: IPL1-108-01-L-D-RE1-K-WT; SAMTEC_IPL1-108-01-L-D-RE1-K-WT
C1, C3, C4, C6: 1 uF; CP_Radial_D5.0mm_P2.00mm
C2, C5: 10 uF; CP_Radial_D10.0mm_P5.00mm
C7: 47 uF; CP_Radial_D4.0mm_P2.00mm
D1, D2, D3, D4, D5, D6, D7, D8, D9, D10, D11, D12, D13, D14, D15, D16: MBR0540; D_DO-15_P15.24mm_Horizontal
IFD97_SPT1, IFD97_SPT2: IPL1-102-01-X-D-RE1-K-WT; SAMTEC_IPL1-102-01-X-D-RE1-K-WT; PARTREV A
IFE91D_2, IFE91D_SPT1: IPL1-102-01-L-S-RE1-K-WT; SAMTEC_IPL1-102-01-L-S-RE1-K-WT
LEDSPT1, LEDSPT2: Conn_01x02; R_Axial_DIN0204_L3.6mm_D1.6mm_P2.54mm_Vertical
LED_Logic_Harness1: IPL1-102-01-X-D-RE1-K-WT; SAMTEC_IPL1-102-01-X-D-RE1-K-WT; PARTREV A
Laser_Power_Pins1: IPL1-102-01-L-S-RE1-K-WT; SAMTEC_IPL1-102-01-L-S-RE1-K-WT
MOTOR_DRIVER1: Conn_02x08_Counter_Clockwise; Motor_Driver_A4988
Motor_CTL_Pins1: IPL1-102-01-L-S-RE1-K-WT; SAMTEC_IPL1-102-01-L-S-RE1-K-WT
Motor_Power_Pins1: IPL1-102-01-L-S-RE1-K-WT; SAMTEC_IPL1-102-01-L-S-RE1-K-WT
Motor_Wires1: IPL1-102-01-X-D-RE1-K-WT; SAMTEC_IPL1-102-01-X-D-RE1-K-WT; PARTREV A
OP07C_1, OP07C_2: Conn_02x04_Counter_Clockwise; DIP-8_W7.62mm
Q1, Q2, Q3, Q4, Q5, Q6, Q7, Q8, Q9, Q10, Q11, Q12, Q13, Q14, Q15, Q16: Q_NMOS_GDS; TO-220-3_Vertical
R1, R5: 2.4K Ω; R_Axial_DIN0207_L6.3mm_D2.5mm_P7.62mm_Horizontal
R2, R6: 1K Ω; R_Axial_DIN0207_L6.3mm_D2.5mm_P7.62mm_Horizontal
R3, R7: 47K Ω; R_Axial_DIN0207_L6.3mm_D2.5mm_P7.62mm_Horizontal
R4, R8: 56 Ω; R_Axial_DIN0207_L6.3mm_D2.5mm_P7.62mm_Horizontal
R9, R10, R11, R12, R13, R14, R15, R16, R17, R18, R19, R20, R21, R22, R23, R24, R25, R26: 220 Ω; R_Axial_DIN0204_L3.6mm_D1.6mm_P7.62mm_Horizontal
Valve_Connector1: IPL1-116-01-X-D-RE1-K-WT; SAMTEC_IPL1-116-01-X-D-RE1-K-WT
XTRA_LED_SPT1, XTRA_LED_SPT2: IPL1-102-01-L-S-RE1-K-WT; SAMTEC_IPL1-102-01-L-S-RE1-K-WT

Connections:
/+12V: 12V_Power_pins1.01, C7.1, D1.1 (K), D2.1 (K), D3.1 (K), D4.1 (K), D5.1 (K), D6.1 (K), D7.1 (K), D8.1 (K), D9.1 (K), D10.1 (K), D11.1 (K), D12.1 (K), D13.1 (K), D14.1 (K), D15.1 (K), D16.1 (K), MOTOR_DRIVER1.8, Valve_Connector1.01, Valve_Connector1.03, Valve_Connector1.05, Valve_Connector1.07, Valve_Connector1.09, Valve_Connector1.11, Valve_Connector1.13, Valve_Connector1.15, Valve_Connector1.17, Valve_Connector1.19, Valve_Connector1.21, Valve_Connector1.23, Valve_Connector1.25, Valve_Connector1.27, Valve_Connector1.29, Valve_Connector1.31
/D97_OUT_1: IFD97_SPT1.02, OP07C_1.2
/D97_OUT_2: IFD97_SPT2.02, OP07C_2.2
/E91D_1_SOURCE: IFE91D_SPT1.01, R4.2
/E91D_2_SOURCE: IFE91D_2.01, R8.2
/GND: 12V_Power_pins1.02, C1.2, C2.2, C3.2, C4.2, C5.2, C6.2, C7.2, IFD97_SPT1.01, IFD97_SPT1.03, IFD97_SPT2.01, IFD97_SPT2.03, IFE91D_2.02, IFE91D_SPT1.02, LEDSPT1.2, LEDSPT2.2, Laser_Power_Pins1.02, MOTOR_DRIVER1.1, MOTOR_DRIVER1.7, MOTOR_DRIVER1.10, MOTOR_DRIVER1.12, Motor_Power_Pins1.02, OP07C_1.4, OP07C_2.4, Q1.3 (S), Q2.3 (S), Q3.3 (S), Q4.3 (S), Q5.3 (S), Q6.3 (S), Q7.3 (S), Q8.3 (S), Q9.3 (S), Q10.3 (S), Q11.3 (S), Q12.3 (S), Q13.3 (S), Q14.3 (S), Q15.3 (S), Q16.3 (S), R2.2, R6.2, XTRA_LED_SPT1.02, XTRA_LED_SPT2.02; also elsewhere on the board
/MOTOR_DIR: MOTOR_DRIVER1.16, Motor_CTL_Pins1.01
/MOTOR_GN: MOTOR_DRIVER1.5, Motor_Wires1.01
/MOTOR_GNWT: MOTOR_DRIVER1.6, Motor_Wires1.02
/MOTOR_PK: MOTOR_DRIVER1.3, Motor_Wires1.03
/MOTOR_PKWT: MOTOR_DRIVER1.4, Motor_Wires1.04
/MOTOR_STEP: MOTOR_DRIVER1.15, Motor_CTL_Pins1.02
/OUT_ARDUINO_SPT1: LED_Logic_Harness1.03, OP07C_1.6, R3.1
/OUT_ARDUINO_SPT2: LED_Logic_Harness1.04, OP07C_2.6, R7.1
/SPT1_LED: LED_Logic_Harness1.01, R25.1
/SPT2_LED: LED_Logic_Harness1.02, R26.1
/V1 GND: D1.2 (A), Q1.2 (D), Valve_Connector1.02
/V1_Gate: ARD2_to_Mosfet_Gates1.01, R9.1; also elsewhere on the board
/V2 GND: D2.2 (A), Q2.2 (D), Valve_Connector1.04
/V2_Gate: ARD2_to_Mosfet_Gates1.02, R10.1; also elsewhere on the board
/V3 GND: D3.2 (A), Q3.2 (D), Valve_Connector1.06
/V3_Gate: ARD2_to_Mosfet_Gates1.03, R11.1; also elsewhere on the board
/V4 GND: D4.2 (A), Q4.2 (D), Valve_Connector1.08
/V4_Gate: ARD2_to_Mosfet_Gates1.04, R12.1; also elsewhere on the board
/V5 GND: D5.2 (A), Q5.2 (D), Valve_Connector1.10
/V5_Gate: ARD2_to_Mosfet_Gates1.05, R13.1; also elsewhere on the board
/V6 GND: D6.2 (A), Q6.2 (D), Valve_Connector1.12
/V6_Gate: ARD2_to_Mosfet_Gates1.06, R14.1; also elsewhere on the board
/V7 GND: D7.2 (A), Q7.2 (D), Valve_Connector1.14
/V7_Gate: ARD2_to_Mosfet_Gates1.07, R15.1; also elsewhere on the board
/V8 GND: D8.2 (A), Q8.2 (D), Valve_Connector1.16
/V8_Gate: ARD2_to_Mosfet_Gates1.08, R16.1; also elsewhere on the board
/V9 GND: D9.2 (A), Q9.2 (D), Valve_Connector1.18
/V9_Gate: ARD2_to_Mosfet_Gates1.09, R17.1; also elsewhere on the board
/V10 GND: D10.2 (A), Q10.2 (D), Valve_Connector1.20
/V10_Gate: ARD2_to_Mosfet_Gates1.10, R18.1; also elsewhere on the board
/V11 GND: D11.2 (A), Q11.2 (D), Valve_Connector1.22
/V11_Gate: ARD2_to_Mosfet_Gates1.11, R19.1; also elsewhere on the board
/V12 GND: D12.2 (A), Q12.2 (D), Valve_Connector1.24
/V12_Gate: ARD2_to_Mosfet_Gates1.12, R20.1; also elsewhere on the board
/V13 GND: D13.2 (A), Q13.2 (D), Valve_Connector1.26
/V13_Gate: ARD2_to_Mosfet_Gates1.13, R21.1; also elsewhere on the board
/V14 GND: D14.2 (A), Q14.2 (D), Valve_Connector1.28
/V14_Gate: ARD2_to_Mosfet_Gates1.14, R22.1; also elsewhere on the board
/V15 GND: D15.2 (A), Q15.2 (D), Valve_Connector1.30
/V15_Gate: ARD2_to_Mosfet_Gates1.15, R23.1; also elsewhere on the board
/V16 GND: D16.2 (A), Q16.2 (D), Valve_Connector1.32
/V16_Gate: ARD2_to_Mosfet_Gates1.16, R24.1; also elsewhere on the board
/XTRA_SPT1_LED: LEDSPT1.1, R25.2, XTRA_LED_SPT1.01
/XTRA_SPT2_LED: LEDSPT2.1, R26.2, XTRA_LED_SPT2.01
/side_one_pin_3: OP07C_1.3, R1.2, R2.1, R3.2
/side_two_pin_three: OP07C_2.3, R5.2, R6.1, R7.2
unnamed: MOTOR_DRIVER1.13, MOTOR_DRIVER1.14
unnamed: Q1.1 (G), R9.2
unnamed: Q2.1 (G), R10.2
unnamed: Q3.1 (G), R11.2
unnamed: Q4.1 (G), R12.2
unnamed: Q5.1 (G), R13.2
unnamed: Q6.1 (G), R14.2
unnamed: Q7.1 (G), R15.2
unnamed: Q8.1 (G), R16.2
unnamed: Q9.1 (G), R17.2
unnamed: Q10.1 (G), R18.2
unnamed: Q11.1 (G), R19.2
unnamed: Q12.1 (G), R20.2
unnamed: Q13.1 (G), R21.2
unnamed: Q14.1 (G), R22.2
unnamed: Q15.1 (G), R23.2
unnamed: Q16.1 (G), R24.2

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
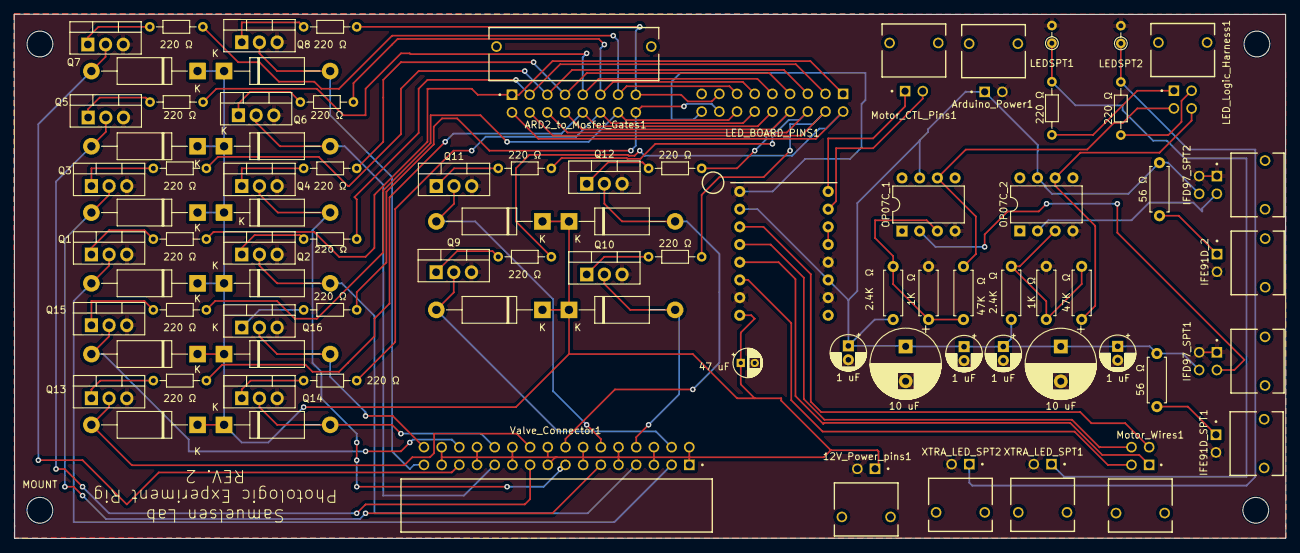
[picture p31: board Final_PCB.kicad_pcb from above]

Board: 2 copper layers, 182.6 x 75.3 mm, 85 parts (1 on the bottom side), 70 nets.

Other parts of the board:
Arduino_Power1: IPL1-102-01-L-S-RE1-K-WT; SAMTEC_IPL1-102-01-L-S-RE1-K-WT
LED_BOARD_PINS1: IPL1-108-01-L-D-RE1-K-WT; SAMTEC_IPL1-109-01-L-D-RE1-K
MOUNT: MountingHole_3.7mm

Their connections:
/GND: Arduino_Power1.02, LED_BOARD_PINS1.18; also elsewhere on the board
/V1_Gate: LED_BOARD_PINS1.01; also elsewhere on the board
/V2_Gate: LED_BOARD_PINS1.02; also elsewhere on the board
/V3_Gate: LED_BOARD_PINS1.03; also elsewhere on the board
/V4_Gate: LED_BOARD_PINS1.04; also elsewhere on the board
/V5_Gate: LED_BOARD_PINS1.05; also elsewhere on the board
/V6_Gate: LED_BOARD_PINS1.06; also elsewhere on the board
/V7_Gate: LED_BOARD_PINS1.07; also elsewhere on the board
/V8_Gate: LED_BOARD_PINS1.08; also elsewhere on the board
/V9_Gate: LED_BOARD_PINS1.10; also elsewhere on the board
/V10_Gate: LED_BOARD_PINS1.11; also elsewhere on the board
/V11_Gate: LED_BOARD_PINS1.12; also elsewhere on the board
/V12_Gate: LED_BOARD_PINS1.13; also elsewhere on the board
/V13_Gate: LED_BOARD_PINS1.14; also elsewhere on the board
/V14_Gate: LED_BOARD_PINS1.15; also elsewhere on the board
/V15_Gate: LED_BOARD_PINS1.16; also elsewhere on the board
/V16_Gate: LED_BOARD_PINS1.17; also elsewhere on the board

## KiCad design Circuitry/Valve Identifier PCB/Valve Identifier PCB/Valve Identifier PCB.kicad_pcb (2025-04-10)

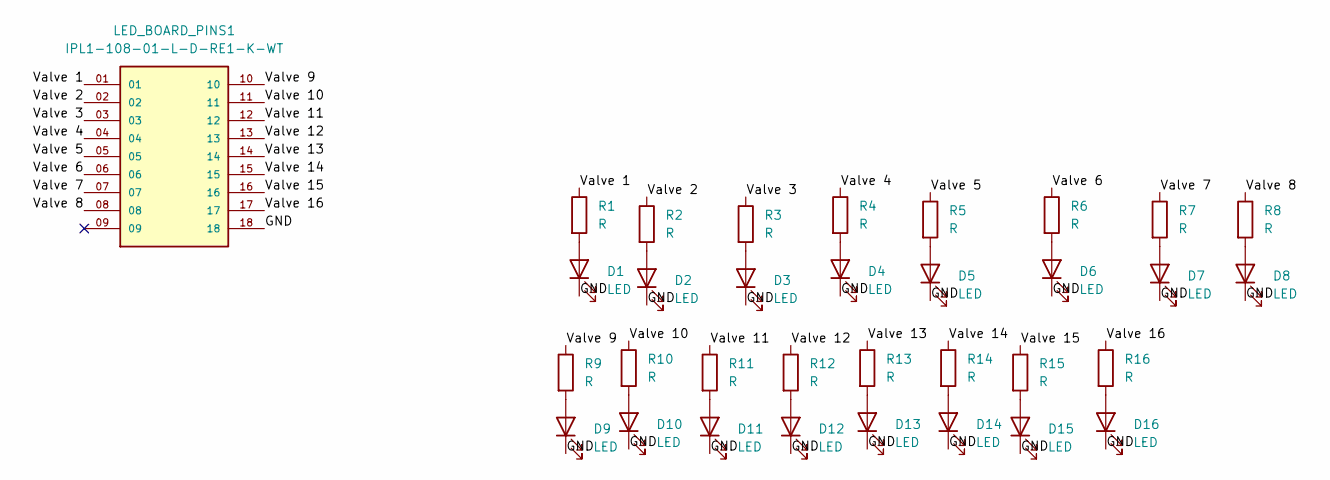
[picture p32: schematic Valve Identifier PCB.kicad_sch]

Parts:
D1, D2, D3, D4, D5, D6, D7, D8, D9, D10, D11, D12, D13, D14, D15, D16: LED; R_Axial_DIN0204_L3.6mm_D1.6mm_P2.54mm_Vertical
LED_BOARD_PINS1: IPL1-108-01-L-D-RE1-K-WT; SAMTEC_IPL1-109-01-L-D-RE1-K; PARTREV A
R1, R2, R3, R4, R5, R6, R7, R8, R9, R10, R11, R12, R13, R14, R15, R16: R; R_Axial_DIN0204_L3.6mm_D1.6mm_P5.08mm_Horizontal

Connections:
/GND: D1.1 (K), D2.1 (K), D3.1 (K), D4.1 (K), D5.1 (K), D6.1 (K), D7.1 (K), D8.1 (K), D9.1 (K), D10.1 (K), D11.1 (K), D12.1 (K), D13.1 (K), D14.1 (K), D15.1 (K), D16.1 (K), LED_BOARD_PINS1.18
/Valve 1: LED_BOARD_PINS1.01, R1.1
/Valve 2: LED_BOARD_PINS1.02, R2.1
/Valve 3: LED_BOARD_PINS1.03, R3.1
/Valve 4: LED_BOARD_PINS1.04, R4.1
/Valve 5: LED_BOARD_PINS1.05, R5.1
/Valve 6: LED_BOARD_PINS1.06, R6.1
/Valve 7: LED_BOARD_PINS1.07, R7.1
/Valve 8: LED_BOARD_PINS1.08, R8.1
/Valve 9: LED_BOARD_PINS1.10, R9.1
/Valve 10: LED_BOARD_PINS1.11, R10.1
/Valve 11: LED_BOARD_PINS1.12, R11.1
/Valve 12: LED_BOARD_PINS1.13, R12.1
/Valve 13: LED_BOARD_PINS1.14, R13.1
/Valve 14: LED_BOARD_PINS1.15, R14.1
/Valve 15: LED_BOARD_PINS1.16, R15.1
/Valve 16: LED_BOARD_PINS1.17, R16.1
unnamed: D1.2 (A), R1.2
unnamed: D2.2 (A), R2.2
unnamed: D3.2 (A), R3.2
unnamed: D4.2 (A), R4.2
unnamed: D5.2 (A), R5.2
unnamed: D6.2 (A), R6.2
unnamed: D7.2 (A), R7.2
unnamed: D8.2 (A), R8.2
unnamed: D9.2 (A), R9.2
unnamed: D10.2 (A), R10.2
unnamed: D11.2 (A), R11.2
unnamed: D12.2 (A), R12.2
unnamed: D13.2 (A), R13.2
unnamed: D14.2 (A), R14.2
unnamed: D15.2 (A), R15.2
unnamed: D16.2 (A), R16.2

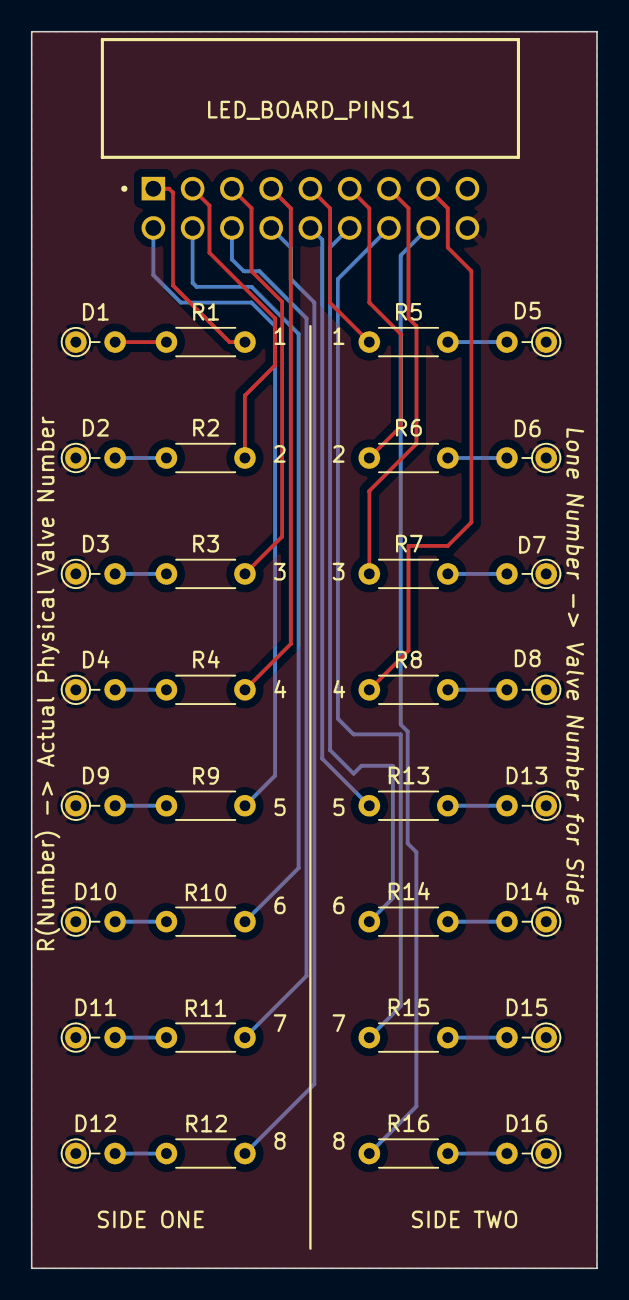
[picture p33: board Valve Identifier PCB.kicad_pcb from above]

Board: 2 copper layers, 36.6 x 80.0 mm, 33 parts (0 on the bottom side), 33 nets.

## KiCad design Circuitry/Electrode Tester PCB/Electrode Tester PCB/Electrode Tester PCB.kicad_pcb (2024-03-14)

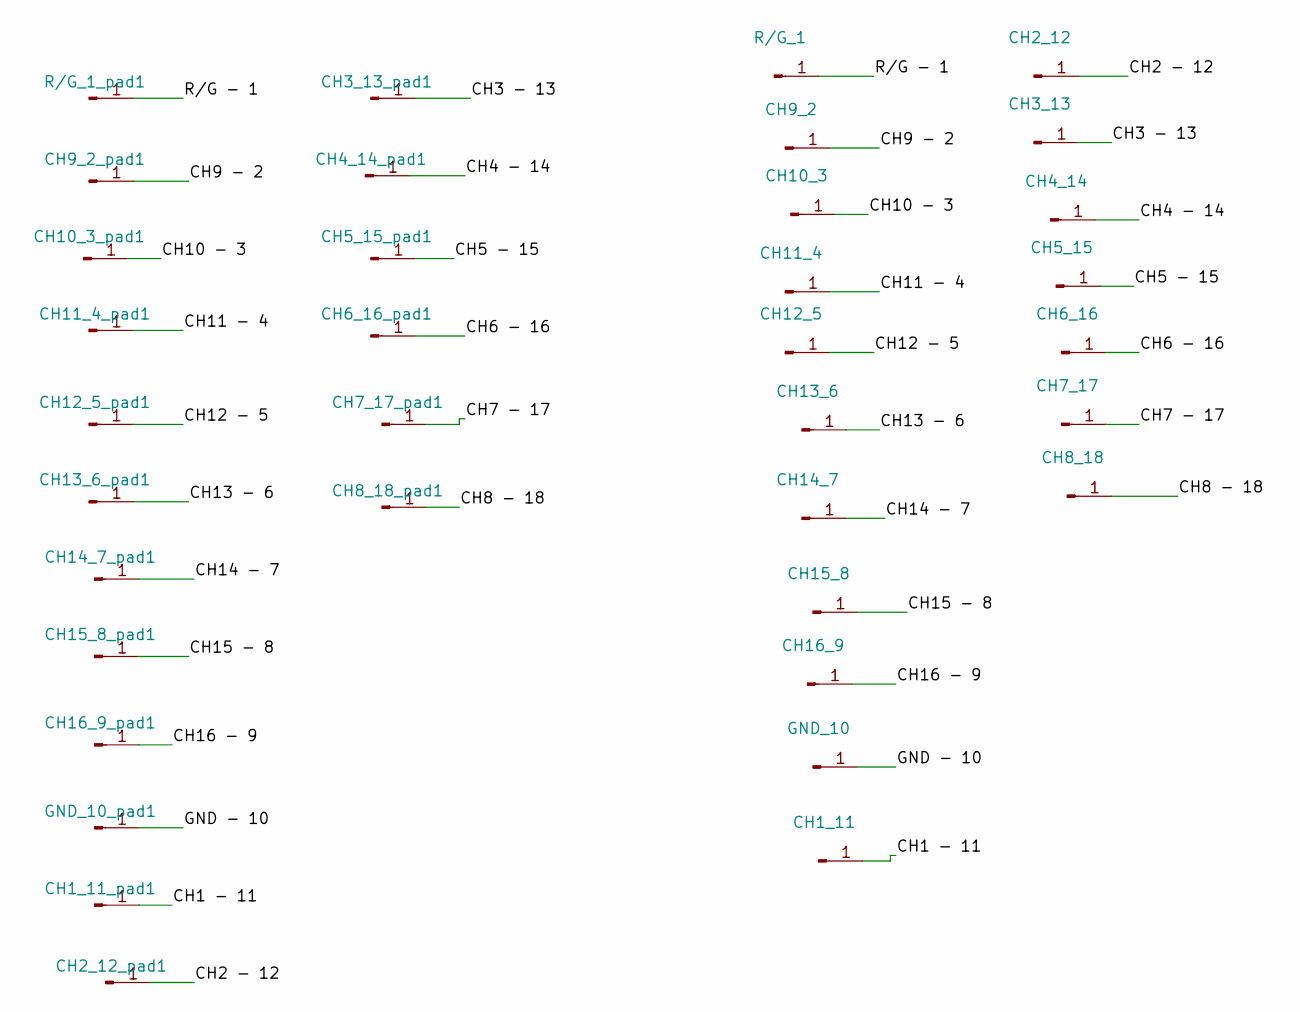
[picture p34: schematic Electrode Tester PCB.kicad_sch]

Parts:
CH1_11, CH2_12, CH3_13, CH4_14, CH5_15, CH6_16, CH7_17, CH8_18, CH9_2, CH10_3, CH11_4, CH12_5, CH13_6, CH14_7, CH15_8, CH16_9: Conn_01x01_Pin; Pin_D1.3mm_L11.0mm
CH1_11_pad1, CH2_12_pad1, CH3_13_pad1, CH4_14_pad1, CH5_15_pad1, CH6_16_pad1, CH7_17_pad1, CH8_18_pad1, CH9_2_pad1, CH10_3_pad1, CH11_4_pad1, CH12_5_pad1, CH13_6_pad1, CH14_7_pad1, CH15_8_pad1, CH16_9_pad1: Conn_01x01_Pin; Test Pad
GND_10: Conn_01x01_Pin; Pin_D1.3mm_L11.0mm
GND_10_pad1: Conn_01x01_Pin; Test Pad
R/G_1: Conn_01x01_Pin; Pin_D1.3mm_L11.0mm
R/G_1_pad1: Conn_01x01_Pin; Test Pad

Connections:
/CH1 - 11: CH1_11.1, CH1_11_pad1.1
/CH2 - 12: CH2_12.1, CH2_12_pad1.1
/CH3 - 13: CH3_13.1, CH3_13_pad1.1
/CH4 - 14: CH4_14.1, CH4_14_pad1.1
/CH5 - 15: CH5_15.1, CH5_15_pad1.1
/CH6 - 16: CH6_16.1, CH6_16_pad1.1
/CH7 - 17: CH7_17.1, CH7_17_pad1.1
/CH8 - 18: CH8_18.1, CH8_18_pad1.1
/CH9 - 2: CH9_2.1, CH9_2_pad1.1
/CH10 - 3: CH10_3.1, CH10_3_pad1.1
/CH11 - 4: CH11_4.1, CH11_4_pad1.1
/CH12 - 5: CH12_5.1, CH12_5_pad1.1
/CH13 - 6: CH13_6.1, CH13_6_pad1.1
/CH14 - 7: CH14_7.1, CH14_7_pad1.1
/CH15 - 8: CH15_8.1, CH15_8_pad1.1
/CH16 - 9: CH16_9.1, CH16_9_pad1.1
/GND - 10: GND_10.1, GND_10_pad1.1
/R/G - 1: R/G_1.1, R/G_1_pad1.1

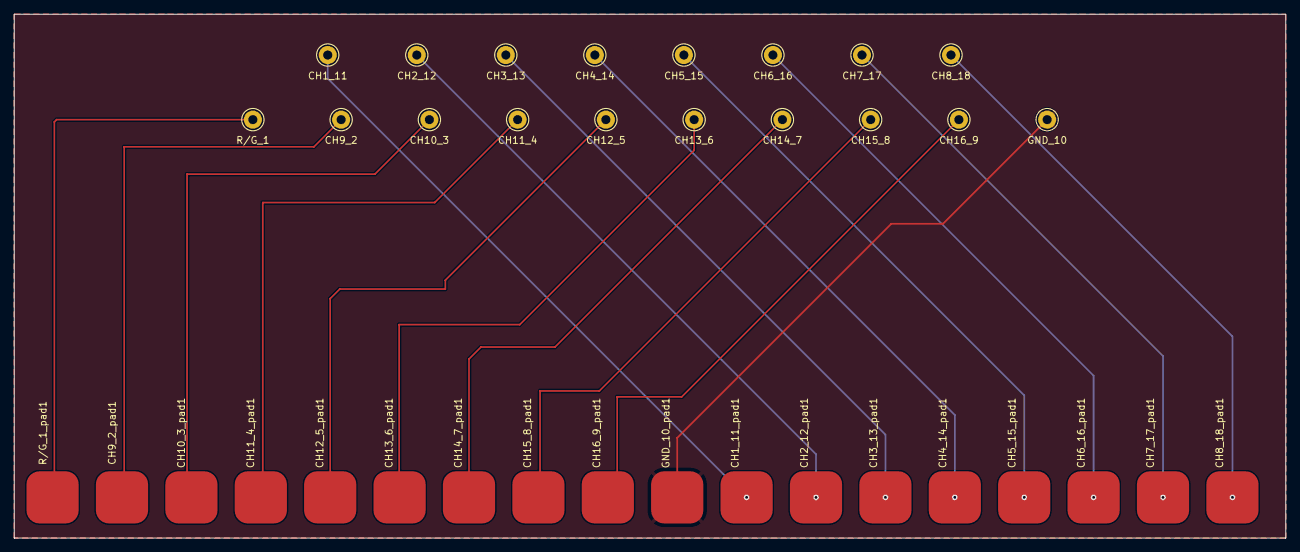
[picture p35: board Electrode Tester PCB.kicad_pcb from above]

Board: 2 copper layers, 182.5 x 75.2 mm, 36 parts (0 on the bottom side), 18 nets.

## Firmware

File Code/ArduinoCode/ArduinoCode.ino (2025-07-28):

#include "./src/optical_detection/optical_detection.h"
#include "./src/valve_control/valve_control.h"
#include "./src/valve_testing/test_valves.h"
#include "./src/reporting/reporting.h"
#include "./src/exp_init/exp_init.h"
#include <AccelStepper.h>
#include <avr/wdt.h>

const unsigned long BAUD_RATE = 115200;

// door stepper motor constants
const int STEPPER_UP_POSITION = 0;
const int STEPPER_DOWN_POSITION = 6000;
const int MAX_SPEED = 5500; 
const int ACCELERATION = 5500;

const uint8_t DIR_PIN = 53;
const uint8_t STEP_PIN = 51;

const uint8_t SIDE_ONE = 0;
const uint8_t SIDE_TWO = 1;

AccelStepper stepper = AccelStepper(1, STEP_PIN, DIR_PIN);

void setup() {
  Serial.begin(BAUD_RATE);

  stepper.setMaxSpeed(MAX_SPEED);
  stepper.setAcceleration(ACCELERATION);

  // Set digital pins 22-29 (PORTA) as outputs (side one valves)
  DDRA = 255; 
  // Set digital pins 30-37 (PORTC) as outputs (side two valves)
  DDRC = 255; 
  
  // set the data direction register to output on pin 4 & pin 5 of the L register
  DDRL |= (1 << LED_BIT_SIDE1);
  DDRL |= (1 << LED_BIT_SIDE2);
  
  // turn each side's (yellow&red) lick indicator LEDs to on
  PORTL |= (1 << LED_BIT_SIDE1);
  PORTL |= (1 << LED_BIT_SIDE2);
  
  DDRB |= (1 << PB4); // digital pin 10 | sends start signal to capacitive arduino.
  DDRH |= (1 << PH5);
  DDRH |= (1 << PH6);

  PORTB &= ~(1 << PB4); // digital 10 | 1 sends start signal
  PORTH &= ~(1 << PH5); // digital 8 | capacitive arduino lick enable set to 0 initially
  PORTH &= ~(1 << PH6); // digital 9 | 1 resets the board (resets lick counters)
  

}

void loop() {
  String command = "\0";
  // define all variables used in experiment runtime scope  
  static String previous_command = "\0";
  
  // structs that hold schedule and duration vectors for the experiment
  static ValveSchedules schedules;
  static ValveDurations durations;
  
  // stores whether motor should open valves or not
  static bool open_valves = false;

  static bool motor_running = false; 

  static bool accept_licks = false;
  
  // use this variable to know if trial start valve opening is occuring. 
  // in other words: do i need to worry about closing the valves? 
  static bool valve_open_trial_start = false;
  // since we support up to 320 trials, 
  // we need more than 2^8 = 255 we use 
  // 16 bit int which provides vals up to 2^16 -1 = 65535
  static uint16_t current_trial = 0;
  
  static unsigned long program_start_time = 0; 
  static unsigned long trial_start_time = 0;
  
  static unsigned long last_poll = 0;
  static unsigned long last_lick_end = 0;
  
  static unsigned long sent_reset_time = 0;
  static unsigned long sent_start_time = 0;

  static bool side_one_pin_state = 0;
  static bool side_one_previous_state = 1;

  static bool side_two_pin_state = 0;
  static bool side_two_previous_state = 1;
  
  // start the time structs off with empty values
  static lickTimeDetails lick_time = {};
  static doorMotorTimeDetails motor_time = {};
  static valveTimeDetails valve_time = {};
  
  // valve time storage for the trial start valve actuations
  static valveTimeDetails trial_start_valve_side_one = {};
  static valveTimeDetails trial_start_valve_side_two = {};

  // side one data variables, used in optical/valve functions like
  // open_valve, close_valve, etc
  static SideData side_one_data{
  SIDE_ONE,
  side_one_pin_state,
  side_one_previous_state,
  durations.side_one,
  schedules.side_one,
  };
  
  // side two struct  
  static SideData side_two_data{
  SIDE_TWO,
  side_two_pin_state,
  side_two_previous_state,
  durations.side_two,
  schedules.side_two,
  };
  
  // a pointer to the side_data for the side that was licked most recently
  static SideData * side_data;
  
  // if reset pin has been high for 3ms or longer reset it. 
  bool reset_pin_high = (PINH & (1 << PH6)) != 0;
  if (reset_pin_high && ((millis() - sent_reset_time) > 2)){
    PORTH &= ~(1 << PH6); // digital 9 | 1 resets the board (resets lick counters)
  }
  
  // if reset pin has been high for 3ms or longer reset it. 
  bool start_pin_high = (PINB & (1 << PB4)) != 0;
  if (start_pin_high && ((millis() - sent_start_time) > 2)){
    PORTB &= ~(1 << PB4); // digital 10, clear start signal bit
  }
  
  if (Serial.available() > 0) {
    // read until the newline char 
    command = Serial.readStringUntil('\n');
  }
  // only process command cases if one has been recieved from the controller
  if (!command.equals("\0")){
    if (command.equals("BEGIN OPEN VALVES")) {
      // begin opening valves from this point forward, 
      // this is called when sample time begins
      open_valves = true;  
      
      PORTH &= ~(1 << PH6); // digital 9 | capacitive arduino reset set to 0 initially, 1 resets
      PORTH |= (1 << PH5); // digital 8 | enable lick counting in sample state
    }
    else if (command.equals("STOP OPEN VALVES")) {
      // stop opening valves
      open_valves = false; 
      
      PORTH &= ~(1 << PH5); // digital 8 | disable lick counting 
      PORTH |= (1 << PH6); // digital 9 | 1 resets the board (resets lick counters)
      
      sent_reset_time = millis();
    }
    else if (command.equals("TRIAL START")){
      trial_start_time = millis(); 
      accept_licks = true;
      valve_open_trial_start = true;
  
      /// open valve for current trial on each spout, disabled for now. need to add ability to enable this as an option
      /// in the controller software. 
      //open_valve(&side_one_data, current_trial);
      //valve_time.valve_open_time = micros();
      //trial_start_valve_side_one.valve_open_time = micros();
      //
      //open_valve(&side_two_data, current_trial);
      //trial_start_valve_side_two.valve_open_time = micros();
    }
    else if (command.equals("T=0")){
      // mark t=0 time for the arduino side
      program_start_time = millis();
      PORTB |= (1 << PB4);

      trial_start_time = program_start_time;
    }
    else if (command.equals("UP")) {
      // tell door motor to move up
      noInterrupts();
      stepper.moveTo(STEPPER_UP_POSITION);
      interrupts();

      motor_time.movement_start = millis();
      motor_time.movement_type = "UP"; 

      previous_command = command;
      motor_running = true;
    }
    else if (command.equals("DOWN")){
      // tell door motor to move down
      stepper.moveTo(STEPPER_DOWN_POSITION);

      motor_time.movement_start = millis();
      motor_time.movement_type = "DOWN"; 

      previous_command = command;
      motor_running = true;
    }
    else if (command.equals("RESET")){
      // reset the board
      wdt_enable(WDTO_1S);
    }
    else if(command.equals("PRIME VALVES")){
      prime_valves();             
    }
    else if (command.equals("TEST VOL")){
      run_valve_test(side_one_data.valve_durations, side_two_data.valve_durations);
    }
    else if (command.equals("OPEN SPECIFIC")){
      control_specific_valves(); 
    }
    else if (command.equals("REC DURATIONS")){
      // receive valve durations from the python controller
      durations = receive_durations();
    }
    else if (command.equals("REC SCHED")){
      // handle recieving program schedule
      schedules = receive_schedules();
    }
    else if (command.equals("REC VAR")){
      // handle recieving program variables (num_stim, num_trials)
      receive_exp_variables();
    }
    else if (command.equals("VER SCHED")){
      schedule_verification(schedules);
    }
    else if (command.equals("VER DURATIONS")){
      durations_verification(durations);
    }
    else {
      Serial.print("Unknown command received: ");
      if (command == "\0"){
        Serial.println("null command");
      }
      Serial.println(command);
    }
  }

  //if(valve_open_trial_start){
  //  close_valve(trial_start_valve_side_one, &side_one_data, current_trial);
  //  close_valve(trial_start_valve_side_two, &side_two_data, current_trial);
  //}

  // check if motor_running first to avoid unneccessary calls to stepper.distanceToGo()
  if (motor_running && stepper.distanceToGo() == 0) {
    // at this stage we have filled movement_start, movement_type, and now movement_end
    motor_time.movement_end = millis();
    report_motor_movement(previous_command, motor_time, program_start_time, trial_start_time);

    if(previous_command.equals("UP")){
      current_trial++;
      accept_licks = false;
    }
    motor_running = false;
  }

  // read current optical sensor pin values, ONLY EVERY 5 MILLISECONDS. We do this to avoid picking up 
  // rapidly changing noise on beam break onset or offset. This was a solution to gh issue #30
  if(millis() - last_poll > 5){
    side_one_previous_state = side_one_pin_state;
    side_two_previous_state = side_two_pin_state;

    side_one_pin_state = (PINL & (1 << OPTICAL_DETECTOR_BIT_SIDE1));
    side_two_pin_state = (PINL & (1 << OPTICAL_DETECTOR_BIT_SIDE2));
    
    last_poll = millis();
  }


  // only if the schedule and durations have been recieved should we detect licks and open valves
  if(schedules.schedules_recieved && durations.durations_recieved){
    // utilized for a sample lick. we only move on from a lick once both valve close time AND 
    // lick finish time have been marked.
    static bool handling_lick = false;
    static bool lick_marked = false;
    static bool valve_marked = false;

    // this is used to 'lock' a mode in so that if a lick begins in ttc it is 
    // guaranteed to finish there. same applies to 'sample' (open_valves)
    static bool ttc_lick = true;
    
    if (accept_licks && (!handling_lick)){
      // if no previous lick or valve movement is being handled
      bool lick_start_one = lick_started(&side_one_data); 
      bool lick_start_two = lick_started(&side_two_data);
    
      // reject licks if that start before 90 seconds after last lick has ended.
      if(millis() - last_lick_end > 90){
        if (lick_start_one || lick_start_two){
          if(lick_start_one){
            side_data = &side_one_data;
          }else{
            side_data = &side_two_data;
          }
          // record lick start time 
          lick_time.lick_begin_time = millis();
          handling_lick = true;

          ttc_lick=true;

          if (open_valves){
            ttc_lick =false;
            open_valve(side_data, current_trial);
            valve_time.valve_open_time = micros();
          }
        }
      }
    }
    else if(handling_lick){
      // check for lick end / valve end and record data
      if (ttc_lick) {
        // insert a close_all call here, because when we tell the arduino to stop opening valves 
        // (make open_valves false), we also cease closing them. This can stick a valve open. Closing all here should 
        // resolve this.
        // we also set lick_market and valve_marked to false to reset the slate for when we return to open_valves state.
        close_all();
        lick_marked = false;
        valve_marked = false;

        if (lick_ended(side_data)){ 
          lick_time.lick_end_time= millis();
          last_lick_end = lick_time.lick_end_time;
          // in the case that we WERE in open valves, but moved out of a sample time without
          handling_lick = false;
          report_ttc_lick(side_data->SIDE, lick_time, program_start_time, trial_start_time);
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

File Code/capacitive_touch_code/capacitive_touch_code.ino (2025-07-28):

// —————— Counters & state ——————
int port_1_val = 0;
int port_2_val = 0;

bool port_1_prev_state = false;
bool port_2_prev_state = false;

bool port_1_state = false;
bool port_2_state = false;




void setup() {
  Serial.begin(115200);

  // QT breakout pins (using PORTB bits 0 and 2)
  DDRB &= ~(1<<PB0); // digital 53
  DDRB &= ~(1<<PB2); // digital 51


  DDRG &= ~(1 << PG2); // digital 39, enable signal. will not count unless this goes high.
  DDRG &= ~(1 << PG0); // digital 41, reset signal. will print currently held values of both pins when high. 
  
  DDRB &= ~(1 << PB4); // digital 10, start signal. will stamp program start time when high.
}

void loop() {
  static int current_trial_num = 1;

  static unsigned long last_poll = 0;
  static unsigned long last_lick_end = 0;
  
  static unsigned long last_reset = 0;
  

  static unsigned long side_1_start = 0;
  static unsigned long side_1_end = 0;
  static unsigned long side_2_start = 0;
  static unsigned long side_2_end = 0;
  
  static unsigned long program_start_time = 0;
  static bool program_start_recieved = 0;

  static unsigned long low_start_time = 0;
  static bool port_1_falling_edge = false;
  static bool port_2_falling_edge = false;
  

  // utilized for a sample lick. we only move on from a lick once both valve close time AND 
  // lick finish time have been marked.
  bool accept_licks = (PING & (1 << PG2)) != 0;
  
  // only reset when PG0 is high, ensure that we don't reset too often.
  bool reset_trials = (PING & (1 << PG0)) != 0;
  
  static bool handling_lick = false;

  bool program_start_signal = (PINB & (1 << PB4)) != 0;
  if (!(program_start_recieved) && program_start_signal){
    program_start_time = millis();
    Serial.print("start time recieved");
    Serial.println(program_start_time );

    program_start_recieved = true;
  }



  if(reset_trials && ((millis() - last_reset) > 30)){
    Serial.print("\n|===============================================|\n");
    Serial.print("\t\tFinished Trial Number -> ");
    Serial.print(current_trial_num);
    Serial.print("\n");
    Serial.print("\t\tSide one licks: ");
    Serial.println(port_1_val);
    
    Serial.print("\t\tSide two licks: ");
    Serial.println(port_2_val);
    Serial.print("\n|===============================================|");

    // reset counts
    port_1_val = 0;
    port_2_val = 0;

    current_trial_num++;

    last_reset = millis();
  }


  // Read current port state as booleans
  if((millis() - last_poll) > 1){
    // update prev state for next loop
    port_1_prev_state = port_1_state;
    port_2_prev_state = port_2_state;

    port_1_state = (PINB & (1 << PINB2)) != 0; // port_1 state reads signal from PB2

    port_2_state = (PINB & (1 << PINB0)) != 0; // port_2 state reads signal from PB2

    last_poll = millis();

  }


  if (accept_licks && (!handling_lick)){
    // reject licks if that start before 60 millis-seconds after last lick has ended.
    if(millis() - last_lick_end > 60){
      if (port_1_state && !port_1_prev_state) {
        // only increment once per touch
        handling_lick = true;
        side_1_start = millis();
      }

      if (port_2_state && !port_2_prev_state) {
        handling_lick = true;
        side_2_start = millis();
      }
    }
  }else if(handling_lick && !(reset_trials)){
    // ——— Port 1: rising‐edge detection ———
    if (!(port_1_state) && port_1_prev_state) {
      low_start_time = millis();
      port_1_falling_edge = true;

    }
    // ——— Port 2: same thing ———
    else if (!(port_2_state) && port_2_prev_state) {
      low_start_time = millis();
      port_2_falling_edge = true;
    }
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

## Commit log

2023-06-06 First commit of all files
    hello github
    [Angle Bracket_Leg Securing Mechanism.SLDPRT, Cage_acryllic_main.SLDPRT, Door.SLDPRT, Glue_helper.SLDPRT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]
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2023-06-08 new angle brackets and nozzle to board mount
    [Mounting Bracket nozzle holder.SLDPRT]
2023-06-08 filament rod
    [New Printer Filament rod.SLDPRT, Stainless_steel_faceplate^Cage_model.SLDPRT]
2023-06-09 housing stl
    [Housing Door.STL, New Printer Filament rod.SLDPRT, tube housing.STL]
2023-06-09 fiber helper
    [Connecting rod to mount bracket.STL, Stainless_steel_faceplate^Cage_model.SLDPRT, fiber helper.STL]
2023-06-13 using 3mf now?
    [Faceplate.DXF, Part1.SLDPRT, faceplate2.DWG, faceplate2.DXF]
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2023-06-14 glue helper v2
    [New Printer Filament rod.SLDPRT, fiber helper.STL]
2023-06-14 helper v3
    [Angle Bracket_Leg Securing Mechanism.SLDPRT, Part1.SLDPRT, fiber helper.STL]
2023-06-15 pi holder v1
    [Pi_Holder.SLDPRT, pi_holder.STL]
2023-06-15 Folder for files prior to versioning
    [Glue_helper.STL, Glue_helper1.STL, Glue_helper2.STL, Housing Door^Cage_model - 6649K286_Tapped Linear Motion Shaft-1.STL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]
2023-06-15 Folders for versions
    [Cage_model - AB90A-Solidworks-2.STL, Cage_model - AB90A-Solidworks-3.STL, Cage_model - AB90A-Solidworks-4.STL, Cage_model - AB90A-Solidworks-6.STL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]
2023-06-15 3D Printing Folder
    [Angle Bracket_Leg Securing Mechanism.SLDPRT, Cage_acryllic_main.SLDPRT, Cage_model - AB90A-Solidworks-2.STL, Cage_model - AB90A-Solidworks-3.STL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]
2023-06-20 vacuum connector
    [Angle Bracket_Leg Securing Mechanism.SLDPRT, Stainless_steel_faceplate^Cage_model.SLDPRT, Stainless_steel_faceplate^Cage_model.STEP, Top Securing Mechanisms.SL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]
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2023-06-23 updating the holder again
    [CNCHolddown.STL]
2023-06-26 screw hole cap
    [Stainless_steel_faceplate^Cage_model.SLDPRT, Top Securing Mechanisms.SLDPRT, screw hole cap.SLDPRT]
2023-06-26 Create screw hole cap.STL
    [screw hole cap.STL]
2023-06-28 updating folder structure
    [Pi_Holder.SLDPRT, Vacuum Holder.SLDPRT, pi_holder.SLDASM]
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2023-06-28 Organizing CNC file structure
    [Faceplate.DXF, faceplate2.DWG, faceplate2.DXF, faceplateHoles.DXF]
2023-06-28 new vacuum connector
    [Big Vacuum Hose Connector.STL, Vacuum Holder.SLDPRT]
2023-06-28 Finalized Rig Acrylic CNC Design
    [Cage Top.SLDPRT, Cage_acryllic_main.SLDPRT, Cage_model_Acrylic_CNC_ASM.SLDASM, Faceplate.SLDPRT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]
2023-06-29 new handle
    [Angle Bracket_Leg Securing Mechanism.SLDPRT, Cage_acryllic_main.SLDPRT, Delrin Head Bolt Mount.SLDPRT, Faceplate.SLDPRT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]
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2023-07-07 locking mechs update
    [Top Locking Mechanisms.SLDPRT]
2023-07-07 update stl securing mechs
    [screw hole cap.SLDPRT]
2023-07-07 update locking mechs
    [Door.SLDPRT, Faceplate.SLDPRT, Top Securing Mechanisms.SLDPRT]
2023-07-07 new nozzle holder
    [Mounting Bracket nozzle holder - Copy of Part6^Assem1_Cage_model-1.STL, Mounting Bracket nozzle holder - Copy of Part6^Assem1_Cage_model-2.STL]
2023-07-07 mounting bracket new stl
    [Mounting Bracket Nozzle Holder .SLDPRT]
2023-07-07 update nozzle holder :)
    [Mounting Bracket Nozzle Holder .SLDPRT]
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2023-07-11 board holes
    [Door.SLDPRT]
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2023-07-18 new bracket nozzle holder
    [Detecter Coupler.SLDPRT, Faceplate.SLDPRT, Mounting Bracket Nozzle holder 1.SLDPRT, Mounting Bracket nozzle holder.SLDPRT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]
2023-07-18 mounting bracket nozzle holder final
    [Door.SLDPRT, Faceplate.SLDPRT, Mounting Bracket Nozzle holder 1.SLDPRT, Mounting Bracket nozzle holder.SLDPRT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]
2023-07-18 nozzle holder stl update
    [Mounting Bracket Nozzle holder 1.SLDPRT]
2023-07-18 nozzle holder final version (hopefully)
    [Mounting Bracket Nozzle holder 1.SLDPRT, tube housing1.SLDPRT]
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2023-07-20 new housing and housing door nc
    [tube housing1.SLDPRT]
2023-07-20 hopefully final nozzle holder
    [Mounting Bracket Nozzle holder 1.SLDPRT]
2023-07-21 Upgraded Rig Python Code
    [tube housing1.SLDPRT]
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2023-08-02 KiKad Cicuitry design + updated py
    [Board Holes.SLDPRT, Final_PCB.kicad_pcb, Final_PCB.kicad_sch]
2023-08-04 PCB Finalized and updates to python program
    [Final_PCB.kicad_pcb]
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2023-08-04 updates to parse
    [output.csv]
2023-08-04 code updates + housing faceplate 2
    [Final_PCB.kicad_pcb, Final_PCB.kicad_sch, output.xlsx]
2023-08-08 almost done with the main program
    [Faceplate.SLDPRT, licks.xlsx, lineup.xlsx]
2023-08-09 trial 2 data
    [output_trial_2.xlsx]
2023-08-09 final pcb and code updates
    [Final_PCB.kicad_pcb, Final_PCB.kicad_sch, output_trial_2.xlsx]
2023-08-10 final python program version 1st draft, PCB final
    [Final_PCB-B_Cu.gbr, Final_PCB-B_Mask.gbr, Final_PCB-B_Paste.gbr, Final_PCB-B_Silkscreen.gbr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]
2023-08-11 nozzle holder test
    [Angle Bracket_Leg Securing Mechanism.SLDPRT, Faceplate.SLDPRT, Mounting Bracket nozzle holder.SLDPRT, Nozzle holder test.STL]
2023-08-14 Update Mounting Bracket Nozzle Holder .STL
    [Mounting Bracket Nozzle Holder .STL]
2023-09-22 laser update
    [Final_PCB.kicad_pcb]
2023-09-22 mega holder
    [arduino_mega_bottom.stl, arduino_mega_top.stl]
2023-10-10 new pcb holder
    [PCB_Holder.STL, Part12.SLDPRT]
2023-10-20 mounting bracket nozzle holder
    [Body1.SLDPRT, Body2.SLDPRT, Body3.SLDPRT, Final_PCB.kicad_pcb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]
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2023-10-27 new holder
    [Cage_model-Split1.SLDPRT, Cage_model.SLDASM, mountingBracketNozzleHolder - mounting bracket holder-1.STL]
2023-11-17 begin refractor
    [licks.xlsx, lineup.xlsx]
2023-12-11 refactoring, moving files
    [output.csv, output.xlsx, output_trial_2.xlsx]
2023-12-12 update requirements
    [lineup.xlsx]
2023-12-12 mega case
    [arduino_mega_bottom.stl, arduino_mega_top.stl]
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2024-01-11 test code
    [1.xlsx, lineup.xlsx]
2024-01-16 Barrier Strips
    [Barrier Strips V1.SLDPRT, Barrier Strips V1.STL]
2024-01-16 bs 1.1
    [Barrier Strips V1.1.STL, Barrier Strips V1.SLDPRT]
2024-01-16 Create Barrier Strips V1.3.STL
    [Barrier Strips V1.3.STL]
2024-01-16 Create Barrier Strips V1.4.STL
    [Barrier Strips V1.4.STL]
2024-01-18 barrel asm
    [Barrier Strips V1.SLDPRT, barrel asm.SLDPRT, barrel asm.STL]
2024-01-18 Update barrel asm.STL
    [barrel asm.STL]
2024-01-18 Update barrel asm.SLDPRT
    [barrel asm.SLDPRT]
2024-01-22 uno case
    [bottom.stl, top.stl]
2024-01-24 teflon tube holder v1
    [Part1.SLDPRT, Teflon Tube Holder.STL]
2024-01-24 holder v 1.1
    [Part1.SLDPRT, Teflon Tube Holder - Part1-1.STL, Teflon Tube Holder - Part2^Teflon tube holder-1.STL, Teflon tube holder.SLDASM]
2024-01-24 moving over fixed cage model
    [3363N14_Miniature Pass-Through Drawer Slides.SLDPRT, Body1.SLDPRT, Body2.SLDPRT, Cage_model-Split1.SLDPRT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]
2024-01-24 teflon tube holder
    [Arduino_mega_case_bottom.f3d, Arduino_mega_case_bottom.step, Arduino_mega_case_top.f3d, Arduino_mega_case_top.step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]
2024-01-24 teflon holder stuff
    [Part1.SLDPRT, Part13^Cage_model.SLDPRT, Teflon tube holder.SLDASM, Teflon tube holder.STL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]
2024-01-25 updates to teflon holder
    [Part1.SLDPRT, Teflon Tube Holder.STL, Teflon tube holder.SLDASM, angler.STL]
2024-01-25 spout arms 2.0
    [Angle Bracket_Leg Securing Mechanism.SLDPRT, Front Plate.SLDPRT, Part13^Cage_model.SLDPRT, Spout Two Arms^Cage_model.STL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]
2024-01-25 updated cage assembly that actually works
    [Part1.SLDPRT, Teflon tube holder.SLDASM, tube holder holder final .SLDPRT]
2024-01-26 spout arms final
    [Spout Arms Final.STL, tube holder holder final .SLDPRT]
2024-01-26 laptop dock
    [Been 4mm.stl, Rubber 4mm.stl]
2024-01-26 delivery mount stls
    [Sliding bracker.STL]
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2024-01-29 updated arms and tube holder fix
    [tube holder holder final .SLDPRT]
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2024-02-22 PCB minor correction/revision
    [Final_PCB.kicad_pcb, Final_PCB.kicad_sch, MB1224-Solidworks.sldprt, OG Rig PCB.kicad_pcb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]
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2024-03-27 fixing adding to df errors
    [lineup.xlsx, notlineup.xlsx]
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2025-02-19 fixing the diaster area
    [A.xlsx, A1.xlsx, experiment schedule 4-10-24 (2).xlsx, experiment schedule 4-10-24 (3).xlsx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]
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2025-03-14 various github issues resolved, ready for windows testing
    [Detailed Event Log Data, 2025-03-14.xlsx, Experiment Schedule, 2025-03-14.xlsx, Individual Lick Data, 2025-03-14.xlsx]
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2025-03-17 resolve issue #25
    [Detailed Event Log Data, 2025-03-17.xlsx, Experiment Schedule, 2025-03-17.xlsx]
2025-03-17 resolve gh issue #17, band-aid solution to issue #26
    [Detailed Event Log Data, 2025-03-17.xlsx, Experiment Schedule, 2025-03-17.xlsx]
2025-03-18 fix issues #20, #26
    [Detailed Event Log Data, 2025-03-17.xlsx, Detailed Event Log Data, 2025-03-18 5 second modes.xlsx, Experiment Schedule, 2025-03-17.xlsx, Experiment Schedule, 2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]
2025-03-20 fix valve test confirm gui #28, remove pathlib dependent code #27, documentation dir
    [Detailed Event Log Data, 2025-03-18 (standard time modes, ~40 second durations).xlsx, Detailed Event Log Data, 2025-03-18 (random intervals 15ms licks) .xlsx, 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]
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2025-04-10 fix breakout board connector orientation
    [Valve Identifier PCB.kicad_pcb]
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
